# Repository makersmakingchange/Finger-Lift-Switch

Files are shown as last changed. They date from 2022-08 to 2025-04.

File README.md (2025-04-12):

# Finger Lift Switch 
The Finger Lift Switch is an assistive switch that is activated by lifting a resting finger upwards. The switch activation distance is approximately 5 mm and the required force is about 5 grams-force.

Connect the cable to an assistive device with a 3.5 mm input jack. The user's lifting fingertip should be placed under the finger lift pad, resting on a lower surface or splint.
When the user raises their lifting finger, the finger lift lever will rotate and activate the switch. The switch will de-activate when the user lowers their lifting finger back to the resting surface. 

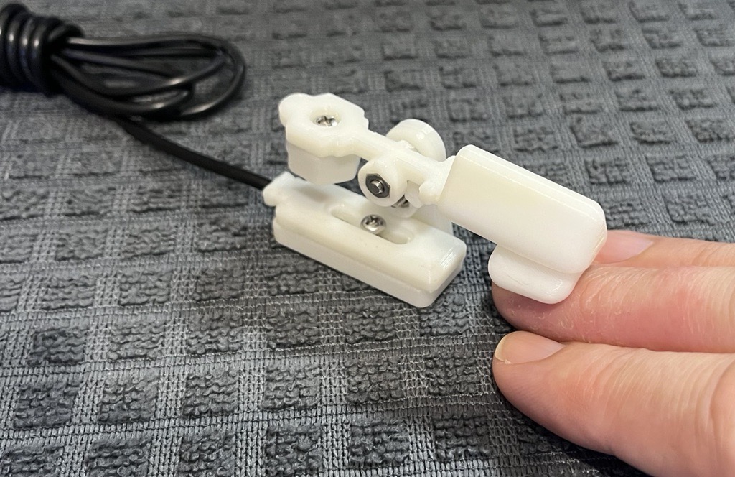
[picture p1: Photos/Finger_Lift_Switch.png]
Picture of Finger Lift Switch.


## More info at
- [Makers Making Change Project Page](https://makersmakingchange.com/project/finger-lift-switch/)

## How to Obtain a Finger Lift Switch
### 1. Do it Yourself (DIY) or Do it Together (DIT)

This is an open-source assistive technology, so anyone is free to build it. All of the files and instructions required to build the Finger Lift Switch are contained within this repository. Refer to the Maker Checklist below.

### 2. Request a build of this device

If you would like to obtain a Finger Lift Switch , you may submit a build request through the [MMC Library Page](https://makersmakingchange.com/project/finger-lift-switch/). The requestor is responsible for the cost of materials and any shipping.

### 3. How to build this device for someone else

If you have the skills and equipment to build this device, and would like to donate your time to create the switch for someone who needs it, visit the [MMC Maker Wanted](https://makersmakingchange.com/maker-wanted/) section.

## Getting Started

### 1. Read the Makers Checklist
Refer to the [Maker's Checklist](/Documentation/Finger_Lift_Switch_Maker_Checklist_v1.0.pdf) for an outline of the steps required to build the device.

### 2. Order the Off-The-Shelf Components

The [Bill of Materials](/Documentation/Finger_Lift_Switch_BOM_v1.0.xlsx) lists all of the parts and components required to build the device. The electronic and hardware component needs to be ordered online.

### 3. Print the 3D Printable components

All of the files and individual print files can be in the [/Build_Files/3D_Printing_Files](/Build_Files/3D_Printing/) folder.

### 4. Assemble the Finger Lift Switch

Reference the [Assembly Guide](/Documentation/Finger_Lift_Switch_Assembly_Guide_v1.0.pdf) for the tools and steps required to build each portion.

## Files
### Documentation
| Document             | Version | Link |
|----------------------|---------|------|
| Design Rationale     | 1.0     | [Finger_Lift_Switch_Design_Rationale](/Documentation/Finger_Lift_Switch_Design_Rationale_v1.0.pdf)     |
| Maker Checklist      | 1.0     | [Finger_Lift_Switch_Maker_Checklist](/Documentation/Finger_Lift_Switch_Maker_Checklist_v1.0.pdf)     |
| Bill of Materials    | 1.0     | [Finger_Lift_Switch_Bill_of_Materials](/Documentation/Finger_Lift_Switch_BOM_v1.0.xlsx)     |
| 3D Printing Guide    | 1.0     | [Finger_Lift_Switch_3D_Printing_Guide](/Documentation/Finger_Lift_Switch_3D_Printing_Guide_v1.0.pdf)     |
| Assembly Guide       | 1.0     | [Finger_Lift_Switch_Assembly_Guide](/Documentation/Finger_Lift_Switch_Assembly_Guide_v1.0.pdf)     |
| User Guide           | 1.0     | [Finger_Lift_Switch_User_Guide](/Documentation/Finger_Lift_Switch_User_Guide_v1.0.pdf)    |
| Changelog            | 1.0     | [Finger_Lift_Switch_Changelog](/Documentation/Finger_Lift_Switch_Changelog_v1.0.pdf)     |

### Design Files
[CAD Files](/Design_Files)

### Build Files
 - [3D Printing Files](/Build_Files/3D_Printing)

## Attribution
Designed by Makers Making Change (Derrick Andrews) in conjunction with Sunnyhill.

## License
Everything needed or used to design, make, test, or prepare the Low Profile Switch is licensed under the CERN 2.0 Permissive license <https://ohwr.org/project/cernohl/wikis/Documents/CERN-OHL-version-2> (CERN-OHL-P) . 

Accompanying material such as instruction manuals, videos, and other copyrightable works that are useful but not necessary to design, make, test, or prepare the Low Profile Switch are published under a Creative Commons Attribution-ShareAlike 4.0 license https://creativecommons.org/licenses/by-sa/4.0/ (CC BY-SA 4.0).

---
<!-- ABOUT MMC START -->
## About Makers Making Change
[Makers Making Change Logo](https://www.makersmakingchange.com/)

Makers Making Change is a program of [Neil Squire](https://www.neilsquire.ca/), a Canadian non-profit that uses technology, knowledge, and passion to empower people with disabilities.

Makers Making Change leverages the capacity of community based Makers, Disability Professionals and Volunteers to develop and deliver affordable Open Source Assistive Technologies.

 - Website: [www.MakersMakingChange.com](https://www.makersmakingchange.com/)
 - GitHub: [makersmakingchange](https://github.com/makersmakingchange)
 - Bluesky: [@makersmakingchange.bsky.social](https://bsky.app/profile/makersmakingchange.bsky.social)
 - Instagram: [@makersmakingchange](https://www.instagram.com/makersmakingchange)
 - Facebook: [makersmakechange](https://www.facebook.com/makersmakechange)
 - LinkedIn: [Neil Squire Society](https://www.linkedin.com/company/neil-squire-society/)
 - Thingiverse: [makersmakingchange](https://www.thingiverse.com/makersmakingchange/about)
 - Printables: [MakersMakingChange](https://www.printables.com/@MakersMakingChange)

### Contact Us
For technical questions, to get involved, or to share your experience we encourage you to [visit our website](https://www.makersmakingchange.com/) or [contact us](https://www.makersmakingchange.com/s/contact).
<!-- ABOUT MMC END -->

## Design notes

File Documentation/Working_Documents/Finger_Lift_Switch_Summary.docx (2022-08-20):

# Title

Finger Lift Switch

## Subtitle

<Short description>

## Device Specifications

Build Time:

< 1hr

1-4 hr

5-10hr

>10hr

Cost:

$0 - $10

$11 - $25

$26 - $50

$51 - $100

$101 - $250

$250+

Stage: Recently Added

Skills: 3D Printing, Soldering

Need: Mobility, Agility/Dexterity

Disability: Mobility / Physical

Difficulty: Intermediate

License: CC-BY-SA

Usages: Environmental Controls, Computer Access, Communication Aids (AAC), Recreation and Leisure

Type: Assistive Switches

Designer: Derrick Andrews

## Device Details

### Overview

The Finger Lift Switch is an assistive switch that is activated by lifting a resting finger upwards. The switch activation distance is approximately 5 mm and the required force is about 5 grams-force.

### Usage

Connect the cable to an assistive device with a 3.5 mm input jack. The user’s lifting fingertip should be placed under the finger lift pad, resting on a lower surface or splint.

When the user raises their lifting finger, the finger lift lever will rotate and activate the switch. The switch will de-activate when the user lowers their lifting finger back to the resting surface.

### Cost

The cost of components for a single switch is approximately $11 CAD. However, obtaining the minimum quantities for a single build will bring the materials costs to $66 CAD.

### Build Instructions

The Finger Lift Switch consists of 3D printed parts and electronic components. The Assembly Guide is available at the GitHub repository.

#### Skills Required

- 3D Printing
- Soldering
- Assembling screws

#### Time Required

3D Printing Time: 1hr 30m

Assembly Time: 30m

#### Tools

- Soldering Iron (fine tip)
- 60/40 rosin core electrical solder
- Medium size Phillips screwdriver (type #1)
- Side cutters
- Wire strippers
- Super glue (gel type is best)
- Hot melt glue gun (low temp type)
- Permanent felt marker (fine tip)
- Needle nose pliers
- Sturdy metal tweezers
- Multimeter (with continuity reading capability)

#### Components

- 1X Ball Bearing: Type MR85ZZ (8 mm OD 5 mm ID)
- 2X 5 mm x 1 mm Magnets (Neodymium)
- 1X Reed Switch (Glass) Contact Normally Open (N/O) Magnetic Induction Switch (2 mm × 14 mm)
- 2X M3 x 8 mm Stainless Steel screws (Base & Base Cap screws)
- 1X M3 x 10 mm Stainless Steel screw (Counterweight screw)
- 1X M3 x 12 mm Stainless Steel screw (Bearing Screw)
- 1X M3 x 16 mm Stainless Steel screw (Balance screw)
- 5X M3 Stainless Steel Nut
- 1X 1/4-20 (Imperial size) Nut
- 1X 5-foot mono audio cable with 3.5 mm male phono plug

#### 3D Printing

- 1X Finger Lift Lever (3D)
- 1X Balance Screw Holder (3D)
- 1X Counterweight Nut Holder (3D)
- 1X Bearing Base (3D)
- 1X Bearing Base Cap (3D)
- 1X Reed Switch Plate (3D)

### Design

This design was created using OpenSCAD.

### Attribution

Designed by Makers Making Change (Derrick Andrews) in conjunction with Sunnyhill.

© 2022 by Neil Squire. This work is licensed under the CC BY SA 4.0 License: http://creativecommons.org/licenses/by-sa/4.0 Files available at https://makersmakingchange.com/project/finger-lift-switch/ Page 1 of 2

V1.0 | JULY 2022 Finger Lift Switch Summary

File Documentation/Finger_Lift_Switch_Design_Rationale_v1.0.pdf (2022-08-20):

V1.0 | July 2022

## FINGER LIFT SWITCH

## DESIGN RATIONALE

© 2022 by <Neil Squire Society >. This work is licensed under the CC BY SA 4.0 License: http://creativecommons.org/licenses/by-sa/4.0
Files available at https://makersmakingchange.com/project/finger-lift-switch/ | Page 1 of 6

### Introduction

The Finger Lift Switch was born from the request of Occupational Therapists working at SunnyHill Children’s Hospital in Vancouver British Columbia. The OTs were seeking an assistive switch capable of being operated by a very young child, who was unable to press down on conventional push button assistive switches. It was noticed that the child was able to lift some finger, albeit, with minimal force.

The intended users of the MMC Finger Lift Switch are people who experienced difficulties pressing downwards on conventional switches, but are able to lift fingers, even with minimal limited force.

### Research

While there appear to be no commercial switches that function via finger lifting action directly, there are low force switches that can be operated by a finger with low force.

The “Wearable Finger Switch for Dexterity” sold by Rehab Mart. The Finger Switch by Enabling Devices. The Finger Switch was billed as “A wearable switch for persons with limited mobility. The slightest movement on the switch activates a device” The Finger Switch uses a small metal rod connected to a limit switch, with a 3.5 mm mono cable to trigger to any suitable device. The switch is constructed from a small 1 inch square by half inch injection molded case.

https://www.rehabmart.com/product/finger-switch-32073.html

The “Adaptive Finger Switch” by GlassOuse

https://glassouse.com/product-category/g-switch-series

The Lift Switch by Stan Cassidy Centre for Rehabilitation (SCCR)

http//www.stancassidy.ca

This is not an actual lift switch, but a switch output inverter, which makes the output state of the switch into its opposite. Note, that virtually all switch inverter circuits register as “on” when the user is not present, as their finger (or hand) is not resting on the switch to maintain the “off” state. This could be problematic in some situations.

## DESIGN RATIONALE

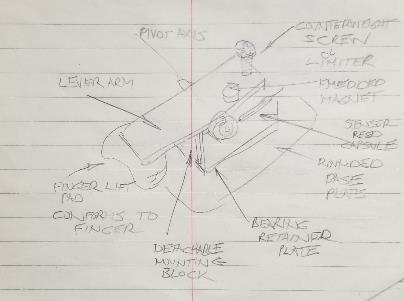
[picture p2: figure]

Files available at https://makersmakingchange.com/project/finger-lift-switch/ | Page 2 of 6

### Requirements

### Goals

G01 | An assistive switch that is activated by a finger lifting action.
G02 | To make the switch operate with minimal force, as in nearly unnoticeable to the user.
G03 | To make the switch operable in many different orientations i.e., minimally sensitive to gravity.

### Functional Requirements

F01 | The switch must activate when a finger lift is detected, but not when user’s hand is removed.
F02 | The switch must operate at angles from zero to at least 45 degrees from horizontal
F03 | The switch must be capable of activation with an operator force of less than 1 gram.

### Non-functional Requirement

NF0 1 | The switch should be narrow enough to allow at least 3 such switches to be operated by a user’s hand, though ideally, 5 (one for every finger).
NF0 2 | The switch must not require a battery.

### Constraints

C01 | The MMC Finger Lift Switch must be able to be constructed using basic ‘maker’ tools.
C02 | The MMC Finger Lift Switch should be able to be disinfected using detergent and alcohol.

### Ideation

Early sketch based on discussion of requirements, with staff from Sunny Hill Children’s Hospital.

## DESIGN RATIONALE

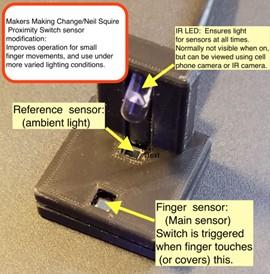
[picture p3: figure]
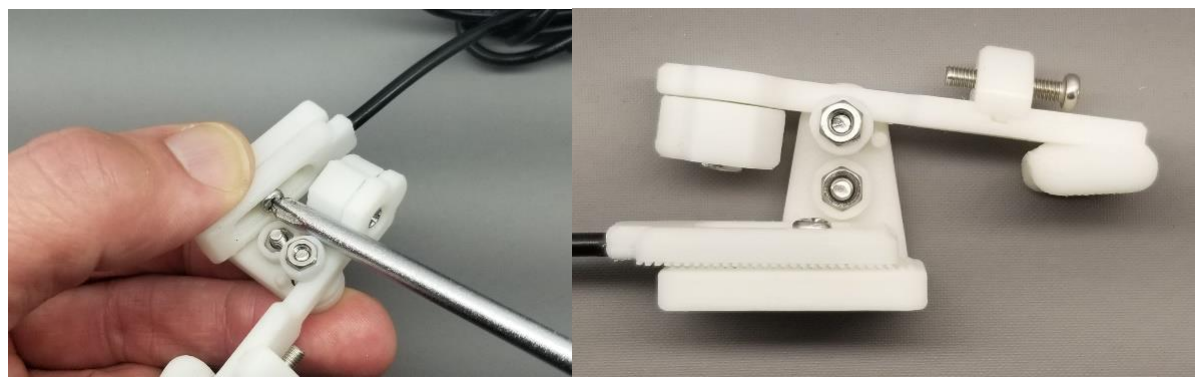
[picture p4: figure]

Files available at https://makersmakingchange.com/project/finger-lift-switch/ | Page 3 of 6

### Conceptual Design

### Concept 1

An initial electronic design of the Finger Lift Switch was created based on parameters given by the occupational therapist of the intended user. The original device was created using scraps of laser cut acrylic, nylon bushing, magnet, and a reed switch. The goal would be to create a final version using 3D printing methods.

### Concept 2

From a video of the user operating the initial optical design, it was determined the user had enough finger strength to operate a finger lever created based on a child’s ability to lift a finger 8 mm (as determined by occupational therapist of the intended user). The original reed switch version was created using scraps of laser cut acrylic, nylon bushing, and a reed switch. The goal would be to create a final version using 3D printing methods.

### Concept 3

## DESIGN RATIONALE

Files available at https://makersmakingchange.com/project/finger-lift-switch/ | Page 4 of 6

### Prototyping

The first iteration was built quickly, using scrap laser cut plastic parts. It was never intended for long term use, but rather, confirming the method of operation would work for the intended recipient. With feedback from Sunny Hill staff, it became clear the switch was easy to operate for the user, but it would benefit from a longer lever arm and proper bearing, instead of a bushing. It also became clear that making a 3D printable version would be worth the effort.

The second iteration was also the first of the 3D printed versions of the Finger Lift switch. It had a longer lever arm, with an integrated finger pad. It only needed a single magnet to trigger the reed switch, as it still relied on a counterweight to return the lever to the default position.

The use of a bushing worked well in the first implementation and was close to being chosen as the main method of rotation. However, when the design was upscaled the design had issues with the lever sliding out of position on the bushing, so the design was changed to incorporate a bearing instead.

The final major design change was the addition of the magnetic lever return. This came about because the occupational therapist requesting the switch, wanted to try mounting the switch on a hand splint at an angle. When they did so, the counterweight no longer exerted the same degree of force on the lever arm, and the lever arm would become sluggish or end up getting stuck in position. With realization that the switch would be more versatile if orientation wasn’t an issue, the decision was made to change to some form of spring return. Using a pair of repelling magnets seemed like a natural fit, as one magnet was already needed for activation of the reed switch, and the magnets usually came in packages of 10 or more. What’s more, the “spring” repulsion force could be arbitrary, by adjusting the gap between the magnets. To top it all off, using two magnets turned out to be rather serendipitous, as the fixed repulsion magnet primed the reed switch, improving its sensitivity, and making switch return less “sticky”.

## DESIGN RATIONALE

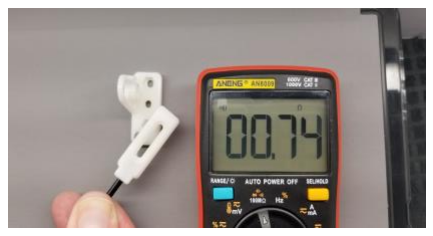
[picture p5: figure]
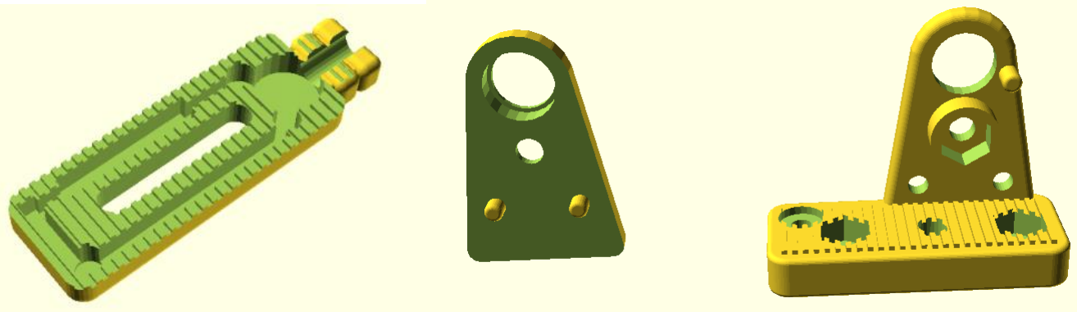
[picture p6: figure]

Files available at https://makersmakingchange.com/project/finger-lift-switch/ | Page 5 of 6

### Testing

### Detailed Design

During operation of the switch, it was noted that the lever arm finger pad sat lower than desired, making it awkward to initially place the user’s finger under the pad. A small post was added in the 3D CAD file to limit the lower end travel of the lever arm. With this change, there is always room under the finger pad to insert a finger prior to use.

### Design Review Improvements

Based on a group design review in July of 2022, several changes were made to the lift switch design. These changes were made for easier assembly, and less chance of breaking the delicate reed switch during construction. The changes made were:

- Widen base, reed switch plate, and solder area cups, to allow easier soldering of the reed switch.
- Remove requirement to bend reed switch wires (reed switch is very brittle glass), and instead, cut the reed switch wires using a jig to set the wire length.
- Trap the balance adjustment screw so it can’t fall out and become a choking hazard.

## DESIGN RATIONALE

Files available at https://makersmakingchange.com/project/finger-lift-switch/ | Page 6 of 6

### Further Opportunities for Improvement

- Change 3D design to minimize number of different screw sizes needed.
- Optimize 3D design and printer placement to produce cleaner holes and minimize the need to trim off excess material i.e., hexagonal holes and increased clearances.
- Placing a screw in the lever arm to allow finger pad resting position to be adjustable.
- Make a version of the switch that uses a readily available paperclip as a bushing, instead of a more difficult to source bearing.
- Allow calibration of the reed switch/magnet gap to be done using a screwdriver, instead of loosening a plate, and repositioning.

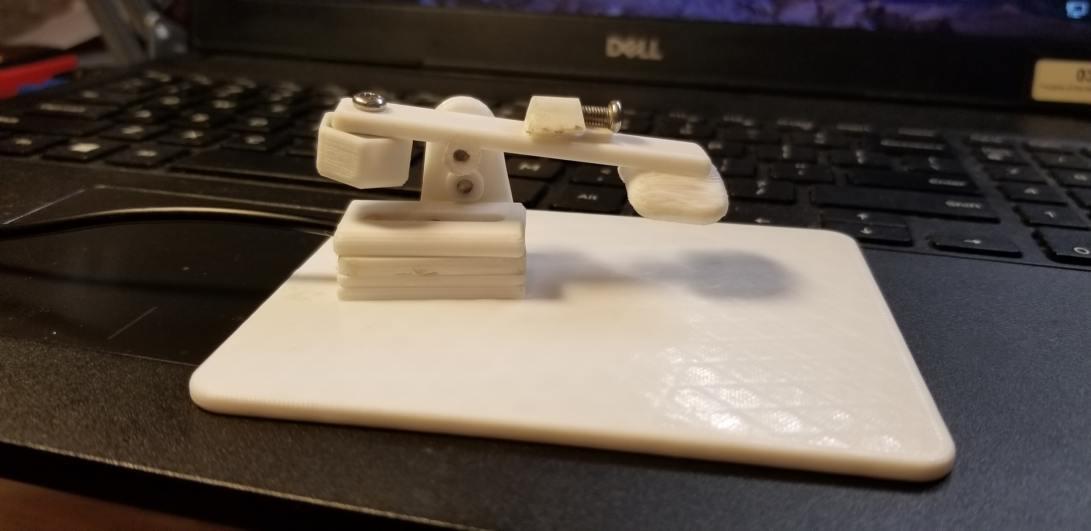
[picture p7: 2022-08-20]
Photos/Later_Finger_Lift_Switch_Prototype.jpg

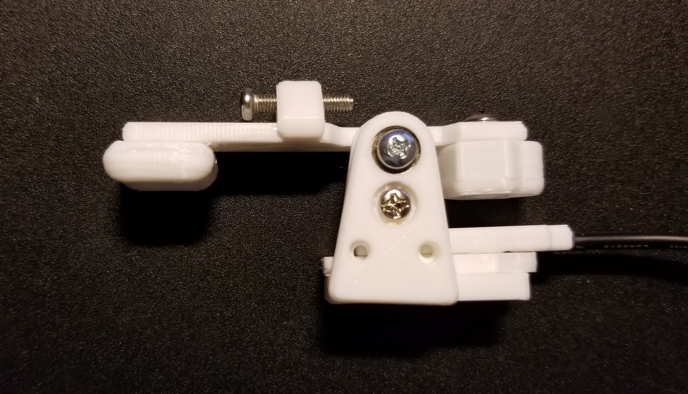
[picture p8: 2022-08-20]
Photos/Finger_Lift_Switch_side.jpg

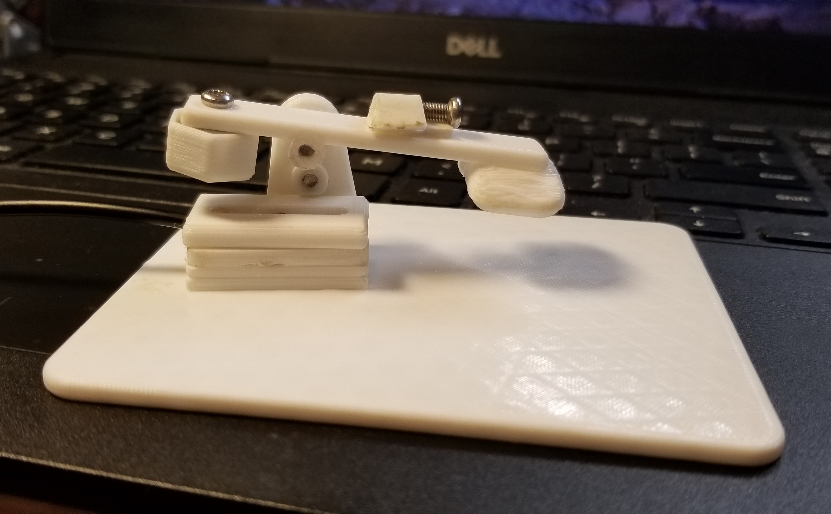
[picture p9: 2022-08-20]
Photos/Finger_Lift_Switch_later_prototype.jpg

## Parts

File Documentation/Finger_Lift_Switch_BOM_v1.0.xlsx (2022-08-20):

Finger Lift Switch for SunnyHill |  |  |  |  |  | $10.37 | $65.62
Part | Description | QTY | QTY/PKG | Min PKGs | Cost/PKG | Unit Cost | Total Cost | Source
Bearing, MR85-2RS, ID: 5 mm, OD: 8 mm, Thickness: 2.5 mm | Bearing | 1 | 10 | 1 | $14.14 | $1.41 | $14.14 | https://www.amazon.ca/MR85-2RS-Groove-Bearings-Double-Sealed/dp/B08JKG5D39
Reed Switch, 2 mm x 14 mm, Normally Open (N/O) | Reed Switch | 1 | 20 | 1 | $11.99 | $0.60 | $11.99 | https://www.amazon.ca/ARTGEAR-Contact-Normally-Magnetic-Induction/dp/B07V2YB2L3
M3 Screw & Nut Kit | M3 Screw & Nut Kit | 1 | 10 | 1 | $11.99 | $1.20 | $11.99 | https://www.amazon.ca/340pcs-Phillips-Stainless-Assortment-Thread/dp/B075RCVVYN?s=hi
Magnet, Neodymium, 5x1mm | Magnet | 2 | 200 | 1 | $13.99 | $0.14 | $13.99 | https://www.amazon.ca/Multi-Use-Refrigerators-Magnets-Whiteboard-Bulletin/dp/B07JDBLVBZ
Nut, 1/4 - 20 medium strength steel hex nut, zinc plated | Mounting Nut | 1 | 1 | 1 | $0.12 | $0.12 | $0.12 | https://www.homedepot.ca/product/paulin-1-4-20-inch-finished-hex-nut-zinc-plated-grade-5-unc-50pcs/1000123233
Cable, M/M, 3.5 mm mono, 10 ft | Mono cable | 1 | 2 | 1 | $12.99 | $6.50 | $12.99 | https://www.amazon.ca/TNP-3-5mm-Mono-Cable-10FT/dp/B01M3NBUD1
Filament, PLA, 1.7 mm, 3850 mm | filament @ $34.99/Kg Density 1.24g/cm3 No Markups | 1 | 1 | 1 | $0.40 | $0.40 | $0.40 | https://www.ic3dprinters.com/3d-printer-job-cost-calculator/#_calc-anchor

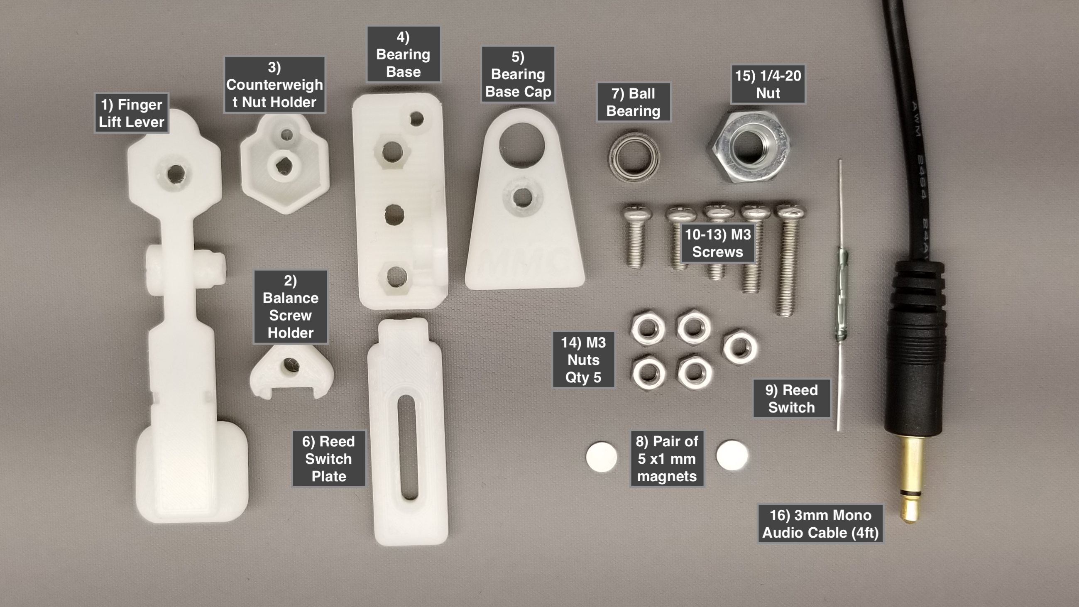
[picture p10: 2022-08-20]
Photos/1_All_Finger_Lift_Switch_parts.jpg

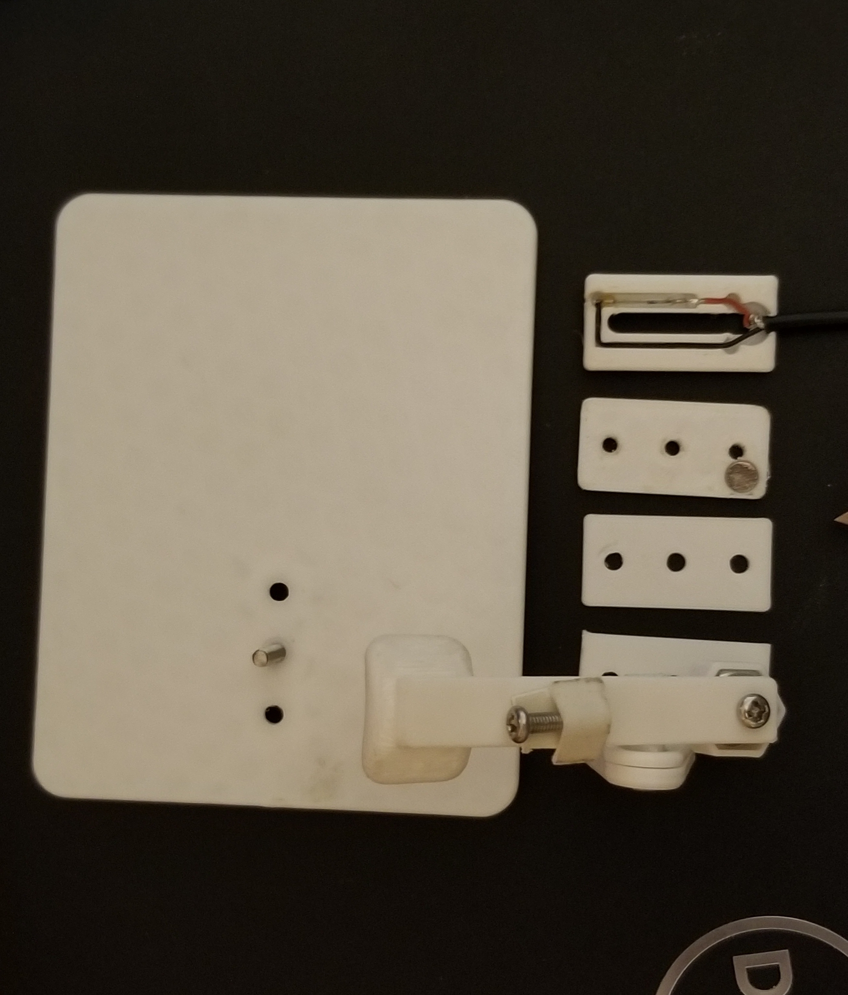
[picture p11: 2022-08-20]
Photos/Later_Finger_Lift_Switch_Parts_set.jpg

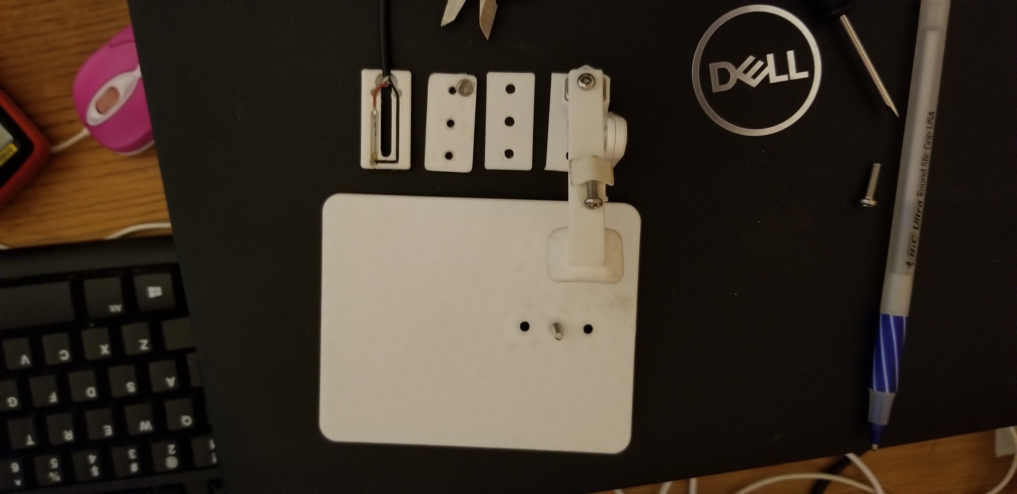
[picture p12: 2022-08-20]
Photos/Early_3D_Switch_Components.jpg

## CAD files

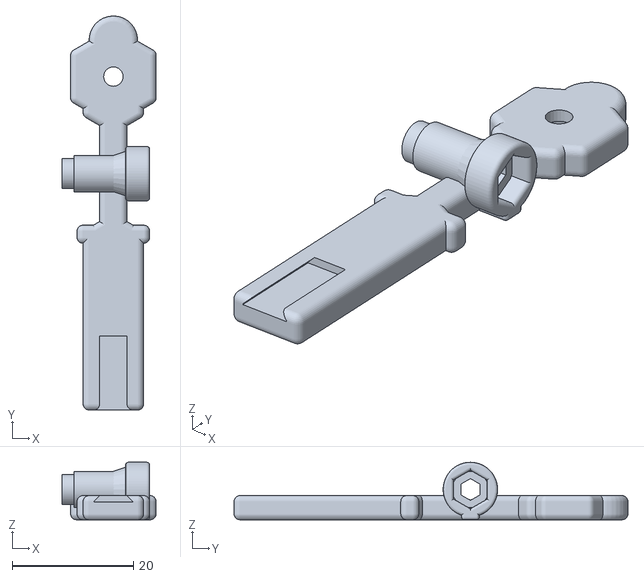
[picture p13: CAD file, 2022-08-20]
Build_Files/3D_Print_Files/FingerLiftArmFn.stl
15.6 x 65.0 x 9.49

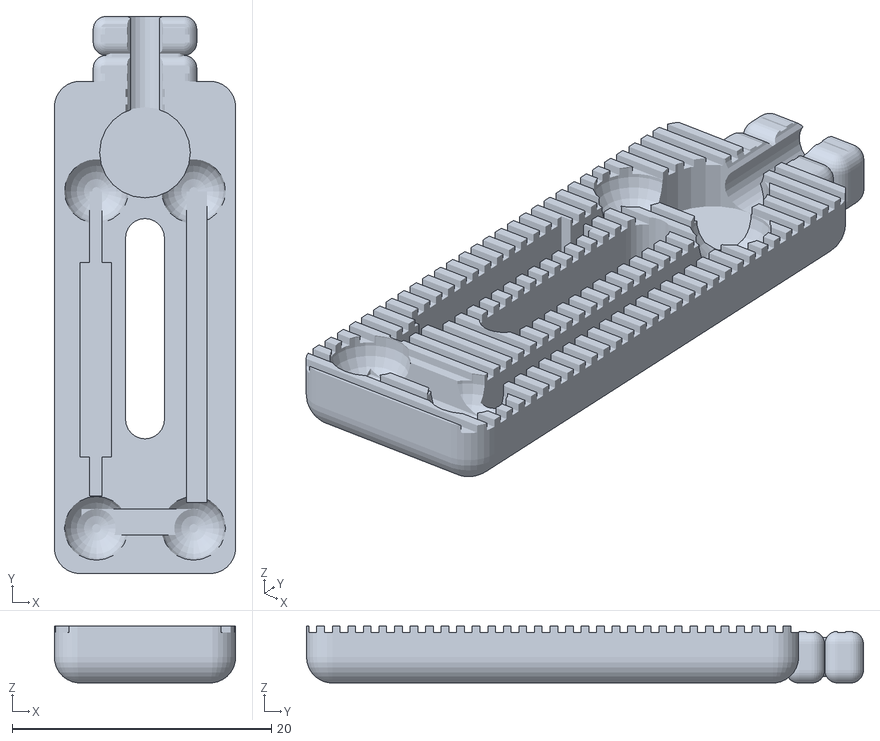
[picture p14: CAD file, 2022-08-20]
Build_Files/3D_Print_Files/ReedSwitchPlateWideFn.stl
14.0 x 43.0 x 4.39

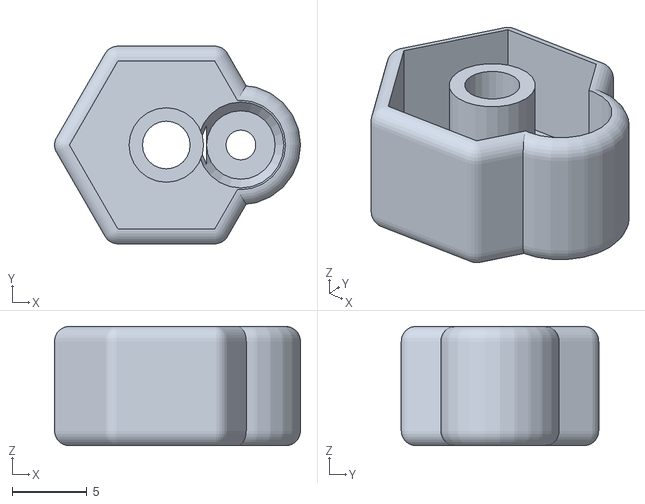
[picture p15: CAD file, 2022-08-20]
Build_Files/3D_Print_Files/CounterWeightHolderFn.stl
16.5 x 13.2 x 7.99

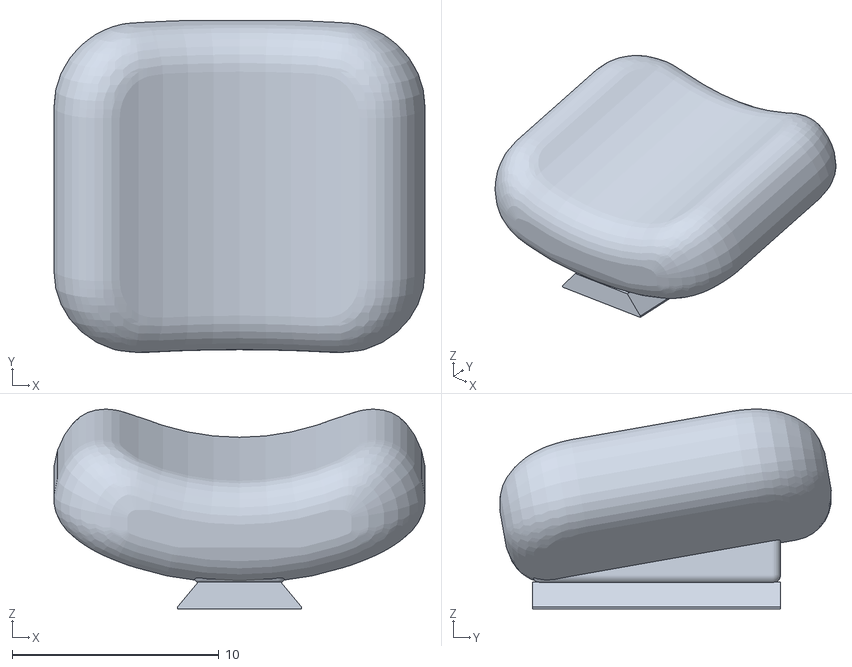
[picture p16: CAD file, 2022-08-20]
Build_Files/3D_Print_Files/FingerLiftPadFn.stl
17.9 x 16.0 x 9.67

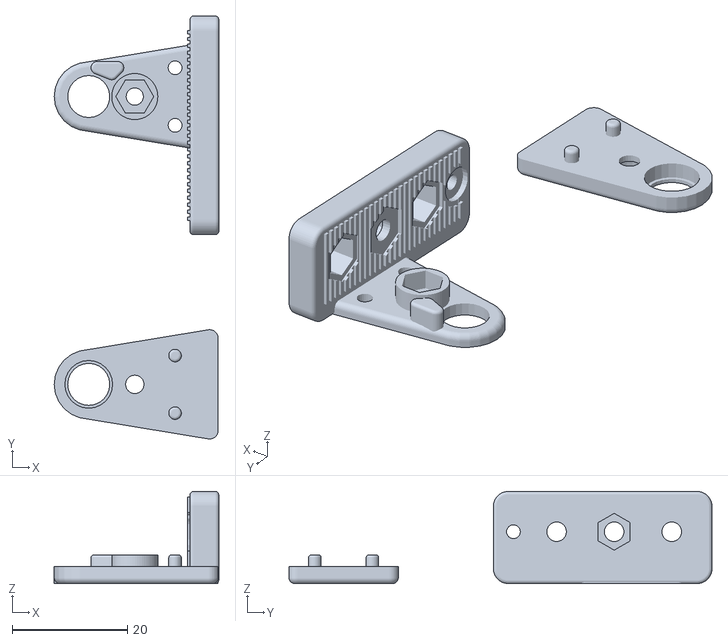
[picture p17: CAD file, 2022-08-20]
Build_Files/3D_Print_Files/FingerBearingBaseFn.stl
28.6 x 73.5 x 16.0

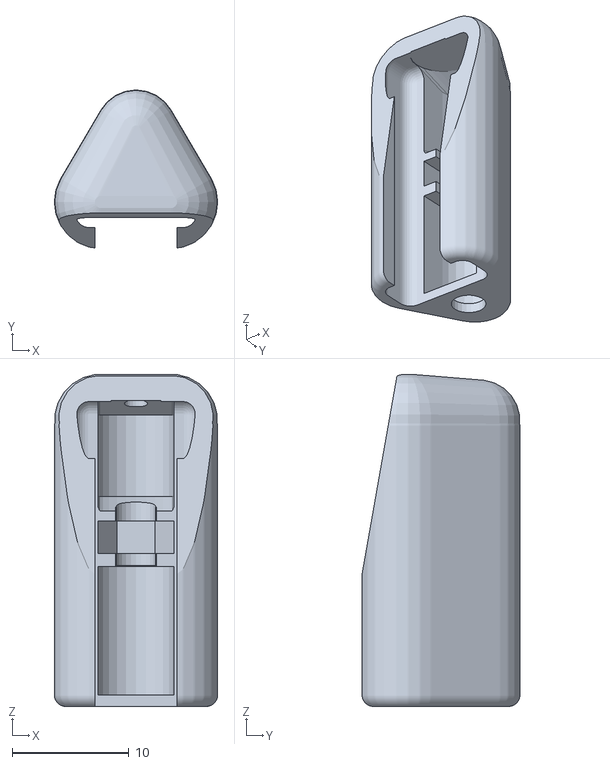
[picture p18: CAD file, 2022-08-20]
Build_Files/3D_Print_Files/BalanceScrewHolderFn.stl
14.0 x 13.5 x 28.5

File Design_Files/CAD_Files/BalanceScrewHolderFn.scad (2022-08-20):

$fn=60;	
holderHeight = 23;

hullDiam=5; //Hull radius diam
balScrewDiam = 3+.4; //Hole for M3 screw + fudge factor
balScrewHeadfDiam = 5.6; //Hole for M3 screw + fudge factor
minkRad = 1;
difference(){

union(){
//FRONT END (hulled)
translate ([0,0,5/2+10])hull() { //nice rounded front end
translate([0,-3.5+5.6,0])sphere(d=hullDiam+2, center = true,$fn=24);//
translate([-3,-4,0])sphere(d=hullDiam+3, center = true,$fn=24);//
translate([3,-4,0])sphere(d=hullDiam+3, center = true,$fn=24);//
}//hull

translate ([0,0,-2])minkowski(){	//TRIANGULAR TUBE
translate ([0,0,5/2])hull() { //rounded bearing mount
translate([0,-3.5+5.6,0])cylinder(d=hullDiam,h=holderHeight, center = true,$fn=24);//
translate([-3,-4,0])cylinder(d=hullDiam+1,h=holderHeight, center = true,$fn=24);//
translate([3,-4,0])cylinder(d=hullDiam+1,h=holderHeight, center = true,$fn=24);//
	
//CircleItems(3,5,30+180)cylinder(d=3,h=5, center = true,$fn=24);//
 
}//hull
sphere(minkRad);


}//minkowski
}//union
//Removals:

//translate([0,-3.5,5.2/2])cube([10.2,3,10], center = true);//original lever cutout
translate([0,-8,5.2/2])cube([7,5,holderHeight+10], center = true);//bottom end cutout for nut access

translate([0,-4,-1])rotate([90,0,0])cutOutSlug();//chop out balance beam area
translate([0,-4.5+5.6,5.2/2])cylinder(d=balScrewDiam,h=10, center = true,$fn=24);//m3 screw holder
translate([0,-4.5+5.6,5.2/2+8.5])cylinder(d=balScrewHDiam,h=9, center = true,$fn=24);//m3 screw Head top
translate([0,-4.5+5.6,5.2/2-8.5+1])cylinder(d=balScrewHeadfDiam,h=10, center = true,$fn=24);//m3 screw Head bottom

translate([0,-4.5+5.6,-12])cylinder(d=balScrewDiam,h=10, center = true,$fn=24);//Screwdriver head access 

translate([0,-4.5+5.6,2.5])rotate([0,0,0])hull(){
cylinder(d=6.5,h=2.8, center = true,$fn=6);//nut cutout
translate([0,-4,0])cylinder(d=6.5,h=2.8, center = true,$fn=6);//nut cutout shifted to make insertion channel
}//hull


//create front screw shaft access 
translate([0,-4.5+5.6,9.5])rotate([0,0,0])hull(){
cylinder(d=6.5,h=7, center = true,$fn=24);//nut cutout
translate([0,-4,0])cylinder(d=6.5,h=9.5, center = true,$fn=24);//nut cutout shifted to make insertion channel
}//hull

//create rear screw head access
translate([0,-4.5+5.6,-5.5])rotate([0,0,0])hull(){
cylinder(d=6.5,h=11, center = true,$fn=24);//nut cutout
translate([0,-4,0])cylinder(d=6.5,h=11, center = true,$fn=24);//nut cutout shifted to make insertion channel
}//hull

translate([0,-4,5.2/2+3])cube([3.5,10,holderHeight-10], center = true);//bottom end cutout for view
translate([0,-7.5,10.5])rotate([-10,0,0])cube([14,3,25], center = true);//angled chop off, to make room for finger lift pad

}//diff
//test area


//
//test nut dummy
//translate([0,-4.5+5.6,2.5])rotate([0,0,0])cylinder(d=6.5,h=2.8, center = true,$fn=6);//nut cutout
//*********** MODULES *****************************

module cutOutSlug(){

difference(){
minkowski(){
translate([0,0,0])roundedCube (8,holderHeight+5,2,0);
 sphere(r=1.2,center=true,$fn=30);//added .2 to loosen grip
}// Mink
//"hard" removals (no rounding) 

//translate([-4.5,0,-1])cube([2,2,3], center = true);
//translate([4.5,0,-1])cube([2,2,3], center = true);
}// diff
}//module


module CircleItems(n,r,myRot)
{
segment=360 / n;
for (i=[1:n])
{
rotate([0, 0, segment*i+myRot])
translate ([r,0,0])
children();
}//for
}//module


module roundedCube (myBoxWidth,myBoxDepth,myBoxHeight,minkRadius)
//** maintains proper 'cube' dimensions due to compensation for object expansion 
//** that normally occurs while using Minkowski operations in OpenSCAD)
{

translate([0,0,0])minkowski(){
cube([myBoxWidth-minkRadius*2,myBoxDepth-minkRadius*2,myBoxHeight-minkRadius*2], center = true);
sphere(r=minkRadius,center=true,$fn=30);
}  //end mink

}//end module roundBottomCube
	
	

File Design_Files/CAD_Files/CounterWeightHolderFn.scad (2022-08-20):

//Software : Counter Weight Holder (component: CounterWeightHolder)
//Developed by : MakersMakingChange  A Neil Squire Society Program
// Code Type: Written in OpenSCAD, a code based, open source 3D CAD modeling environment.
//Original Author: Derrick Andrews
//VERSION: 2.2-beta (July 2022) 
//Copyright Neil Squire Society 2022. 
//LICENSE: This work is licensed under the CC BY SA 4.0 License: http://creativecommons.org/licenses/by-sa/4.0 .

difference(){
	minkowski(){	
	    union(){
		translate([0,0,8/2]) cylinder(d=13,h=6, center = true,$fn=6);//counterweight nut cutout
	    translate([5,0,8/2])cylinder(d=6,h=6, center = true,$fn=24);//magnet cutout
			}//union
		sphere(r=1,center=true,$fn=30);
}  //end mink	n
   //removals
	translate([5,0,8/2+2])cylinder(d=6,h=8, center = true,$fn=24);//**magnet drop in chute
translate([0,0,8/2+2]) cylinder(d=13,h=8, center = true,$fn=6);//counterweight nut cutout

translate([5,0,1.2/2+1])cylinder(d1=4.6,d2=6,h=1.2, center = true,$fn=24);//magnet cutout
 translate([5,0,0])cylinder(d=2,h=10, center = true,$fn=24);//magnet release
cylinder(d=3.2,h=5, center = true,$fn=24);//M3 screw hole
cylinder(d=3.2,h=8, center = true,$fn=24);//M3 screw hole
translate([0,0,-.5])rotate([0,0,30])cylinder(d=6.2,h=2.1, center = false,$fn=6);//M3 nut capture  hole
}
 translate([0,0,5])difference(){

 cylinder(d=5,h=6, center = true,$fn=24);//M3 screw hole
  cylinder(d=3.2,h=6, center = true,$fn=24);//M3 screw hole
	}

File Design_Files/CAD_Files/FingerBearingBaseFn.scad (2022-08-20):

baseBlockHeight =5;
nutPocketHeight =2.4+.6+1;// M3 nut height in mm with .6 extra clearance
nutHexDiam =6 +.4 ; 
//translate([10,73,9])rotate([0,270,180])import("/Users/derrickandrews/My Drive/NSS Office/MMC Finger Lift Review Improvements /ReedSwitchPlateWideProto.stl");


translate([0,0,0])makeBearingCoverPlate();//accepts bearing 
translate([0,50,2])rotate([180,0,0]) makeBearingStand(); //Cover Plate goes on this portion of base
//translate([0,50,2])rotate([180,0,0]) makeBearingBaseOld(); //The main base block original narrow version
translate([7.5,47,9])rotate([180,270,180]) makeBearingBaseNew(); //The main base block wider version
//makeBearingBaseNew(); //The main base block wider version (base default centered here)


module makeBearingBaseNew()
{
difference(){	
union(){

minkowski(){
translate([-1,-2,3.8/2+.5])rotate([0,0,0]) sideRoundedCube(16-1.2,38-1.2,3.8,2);//even better with rounding
sphere(r=.6, center = true,$fn=30);
}  //end mink
translate([0,-2,4.8+.2])ArrayCentItemsVar(1,28,1,1.2)cube([12,.6,.6], center = true);
}//union

//Removals
ArrayCentItemsVar(1,3,0,10)cylinder(d=3.4,h=20, center = true,$fn=24);//Create line of 3 screw holes in base
translate([0,0,3/2-.2])cylinder(d=6.4,h=nutPocketHeight-.5, center = true,$fn=6);//Create center lower nut catch
translate([0,0,(baseBlockHeight+.5)-nutPocketHeight/2+.01])ArrayCentItemsVar(1,2,0,20)cylinder(d=6.4,h=nutPocketHeight, center = true,$fn=6);////Create upper (outer) nut catches

translate([0,0,baseBlockHeight+.2])ArrayCentItemsVar(1,3,0,10)cylinder(d=6.4+2,h=1, center = true,$fn=6);//Remove grip from around screw holes
translate([0,-17.5,5])cylinder(d=5.4,h=2, center = true,$fn=24);//Bore magnet recess
translate([0,-17.5,6])cylinder(d=7,h=2.2, center = true,$fn=24);//Bore magnet recess
translate([0,-17.5,6])cylinder(d=2.4,h=20, center = true,$fn=24);//Create magnet release hole in base
}//diff	
//test cube([14,36,14], center = true);
}



module makeBearingBaseOld()
{
difference(){	
union(){
//translate([6.6,5,-13/2])cube([2,30,17], center = true);	//original Base portion (printed vertically)
//translate([6.6-1.5,5+1,-13/2+1])cube([2+3,30+2,15], center = true);	//new fatter Base portion (printed vertically)
minkowski(){
translate([6.6-1.5,5+1,-13/2+1.5])rotate([90,0,90]) sideRoundedCube(34-1.2,14-1.2,5-1.2,2);//even better with rounding
sphere(r=.6,center=true,$fn=30);
}  //end mink
translate([2.4,6,-5.5])ArrayCentItemsVar(1,26,1,1.2)cube([.6,.6,10], center = true);
}

translate([0,-5-1,-6])rotate([0,90,0])cylinder(d=3.4,h=20, center = true,$fn=24);//Create front hole in base
translate([3.5,-5-1,-6])rotate([0,90,0])cylinder(d=6.4,h=4, center = true,$fn=6);//Bore front screw head countersink in base

translate([0,5-1,-6])rotate([0,90,0])cylinder(d=3.4,h=20, center = true,$fn=24);//Create center hole in base
translate([6.7,5-1,-6])rotate([0,90,0])cylinder(d=6.4,h=5, center = true,$fn=6);//Create center lower nut catch

translate([0,15-1,-6])rotate([0,90,0])cylinder(d=3.4,h=20, center = true,$fn=24);//Create rear hole in base
translate([3.5,15-1,-6])rotate([0,90,0])cylinder(d=6.4,h=4, center = true,$fn=6);//Bore rear screw head countersink in base
	
translate([0,15+4,-6+4])rotate([0,90,0])cylinder(d=2.4,h=20, center = true,$fn=24);//Create magnet release hole in base
//translate([0,15+4,-6+4])rotate([0,90,0])cylinder(d=2.4,h=20, center = true,$fn=24);//Create pseudo magnet 	
translate([2.5,15+4,-6+4])rotate([0,90,0])cylinder(d=5.4,h=2.2, center = true,$fn=24);//Bore magnet recess	

}	

}


module makeBearingCoverPlate()
{

difference(){
minkowski(){	
hull() { //rounded bearing mount
    translate([-15,0,4/2])cylinder(d=10,h=2, center = true,$fn=24);//
    translate([6,8,4/2])cylinder(d=1,h=2, center = true,$fn=24);//Create center side hole
	translate([6,-8,4/2])cylinder(d=1,h=2, center = true,$fn=24);//Create center side hole
}//hull
sphere(r=1,center=true,$fn=30);
}  //end mink
//removals
translate([0,0,3/2+3]) cube([50,30,3], center = true);
translate([-15,0,4/2])cylinder(d=7.3,h=4, center = true,$fn=24);//Create bearing catch hole
translate([-15,0,4/2+.6])cylinder(d=8.3,h=4, center = true,$fn=24);//Create bearing hole	

translate([-7,0,4/2]) cylinder(d=3.2,h=4, center = true,$fn=24);//Create plate cinch hole
translate([-7,0,2/2]) cylinder(d=6.6,h=2, center = true,$fn=24);//Create plate cinch head countersink
 //emboss text
 union(){
  translate([5.5,7.5,0.5])rotate([0,180,90]) linear_extrude(height = 5) {
       text(text = "MMC",font = "Liberation Sans:style=Bold Italic",size = 4.5);
     }//text 
}//union

}//difference


//translate([0,-5,3/2])cylinder(d=2,h=3, center = true,$fn=24);//test post
minkowski(){
translate([0,5,5/2])cylinder(d=1.2,h=4, center = true,$fn=24);//Create center side aligner pin
sphere(r=.5,center=true,$fn=30);
}  //end mink
minkowski(){
translate([0,-5,5/2])cylinder(d=1.2,h=4, center = true,$fn=24);//Create center side aligner pin
sphere(r=.5,center=true,$fn=30);
}  //end mink



}//end module make bearing plate


module makeBearingStand()
{


difference(){
minkowski(){	
hull() { //rounded bearing mount
    translate([-15,0,4/2])cylinder(d=10,h=2, center = true,$fn=24);//
    translate([6,8,4/2])cylinder(d=1,h=2, center = true,$fn=24);//Create center side hole
	translate([6,-8,4/2])cylinder(d=1,h=2, center = true,$fn=24);//Create center side hole
}//hull
sphere(r=1,center=true,$fn=30);
}  //end mink
//removals
translate([0,0,3/2+3]) cube([50,30,3], center = true);
translate([-15,0,4/2])cylinder(d=7.3,h=4, center = true,$fn=24);//Create bearing back catch bore
//translate([-15,0,4/2+.6])cylinder(d=8.3,h=4, center = true,$fn=24);//Create bearing holder bore if needed	
translate([0,5,3/2])cylinder(d=2.4,h=5, center = true,$fn=24);//Create center side hole
translate([0,-5,3/2])cylinder(d=2.4,h=5, center = true,$fn=24);//Create center side hole
translate([-7,0,4/2]) cylinder(d=3,h=4, center = true,$fn=24);//Create plate cinch hole
translate([-7,0,3/2+2]) cube([35,25,3], center = true);//remove unwanted bottom
}//difference
//translate([0,-5,3/2])cylinder(d=2,h=3, center = true,$fn=24);//test post

minkowski(){
difference(){
translate([-7,0,-1]) cylinder(d=7.75,h=4, center = true,$fn=60);//Create screw thread extension
translate([-7,0,0]) cylinder(d=6.4+1.2,h=10, center = true,$fn=6);//Create nut catch below bearing
}//diff
sphere(r=.5,center=true,$fn=30);
}  //end mink

//translate([-14,-5,-1]) cylinder(d=2,h=3, center = true,$fn=24);/Create lever drop limiter post 

minkowski(){
hull(){
translate([-14.5,-4.8,-2])cylinder(d=.8,h=6, center = true,$fn=24);////Create lever drop limiter post: top (rounded)
translate([-11,-4,-2])cylinder(d=.8,h=6, center = true,$fn=24);////Create lever drop limiter post: inside middle(rounded)
translate([-10,-5.6,-2])cylinder(d=.8,h=6, center = true,$fn=24);////Create lever drop limiter post: bottom (rounded)
}

sphere(r=.75,center=true,$fn=30);
}  //end mink

}//end module makeBearingStand()



module basicBox (myBoxWidth,myBoxDepth,myBoxHeight,myWallWidth)
{
difference(){	
cube([myBoxWidth,myBoxDepth,myBoxHeight], center = true); // Build box body
translate([0,0,myWallWidth+.01])cube([myBoxWidth-myWallWidth*2,myBoxDepth-myWallWidth*2,myBoxHeight-myWallWidth*2], center = true); // Mill out box cavity
}//end diff
}//end module basic box
	

module roundedBox (myBoxWidth,myBoxDepth,myBoxHeight,myWallWidth,minkRadius)
//creates hollow rounded bottom box IMPORTANT*** requires module roundBottomCube 
{
difference(){	
roundBottomCube (myBoxWidth,myBoxDepth,myBoxHeight,minkRadius); // Build box body
translate([0,0,myWallWidth+.01])roundBottomCube (myBoxWidth-myWallWidth*2,myBoxDepth-myWallWidth*2,myBoxHeight-myWallWidth*2,minkRadius); //Mill out box cavity
}//end diff
//translate([20,0,myWallWidth+.01])roundBottomCube (myBoxWidth-myWallWidth*2,myBoxDepth-myWallWidth*2,myBoxHeight-myWallWidth*2,minkRadius); // Mill out box cavity
//translate([20,0,myWallWidth+.01])roundBottomCube (myBoxWidth,myBoxDepth,myBoxHeight,minkRadius); // Build box body
}//end module rounded box

//roundBottomCube (myBoxWidth,myBoxDepth,myBoxHeight,minkRadius);


module roundBottomCube (myBoxWidth,myBoxDepth,myBoxHeight,minkRadius)
//** Same as regular cube, but with rounded sides and bottom
//** maintains proper 'cube' dimensions due to compensation for object expansion 
//** that normally occurs while using Minkowski operations in OpenSCAD)
{
union()
{
difference()
{
translate([0,0,minkRadius/2])minkowski(){
cube([myBoxWidth-minkRadius*2,myBoxDepth-minkRadius*2,myBoxHeight-minkRadius], center = true);//Main plate   original cube([90,testSize8,8.5]
sphere(r=minkRadius,center=true,$fn=30);
}  //end mink
translate([0,0,myBoxHeight/2+minkRadius/2]) cube([myBoxWidth,myBoxDepth,minkRadius], center = true);
}

}//end union
}//end module roundBottomCube

//test
//translate ([15,0,0])cube([35,35,35],center=true);
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

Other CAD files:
Design_Files/CAD_Files/FingerLiftArmFn.scad
Design_Files/CAD_Files/FingerLiftPadFn.scad
Design_Files/CAD_Files/ReedSwitchPlateWideFn.scad

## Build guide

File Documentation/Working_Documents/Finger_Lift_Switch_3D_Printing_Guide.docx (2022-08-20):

# 3D Printing Summary

Metrics
Total Print Time (min) | 1:23
Total Number of Components | 6
Typical Total Mass (g) | 7
Typical Number of Print Setups | 1

# 3D Printing Settings

Print File Name | Qty | Total Print Time (hr:min) | Mass (g) | Infill (%) | Support(Y/N) | Layer Height/ Nozzle Diameter(mm) | Notes (orientation, special settings, etc.)
Finger Lift Lever | 1 | 0:19 | 2 | 15 | N | 0.2/0.4 | - Print in orientation given in STL
Balance Screw Holder | 1 | 0:07 | 1 | 15 | N | 0.2/0.4 | - Print in orientation given in STL
Counterweight nut holder | 1 | 0:11 | 1 | 15 | N | 0.2/0.4 | - Print in orientation given in STL
Bearing Base & Bearing Base Cap | 1 | 0:29 | 2 | 15 | N | 0.2/0.4 | - Print in orientation given in STL
Reed Switch Plate | 1 | 0:10 | 1 | 15 | N | 0.2/0.4 | - Print in orientation given in STL

# Customization Options

Specific colours are not a requirement for this device, so device (or components) may be printed in whichever colours the user desires.

# Post-Processing

Remove any stranding or excess material in holes with a hobby knife. Any parts of the Finger Lift Pad that feel rough or scratchy should be lightly sanded with fine sandpaper until smooth to touch.

# Examples of Quality Prints

Finger Lift Lever

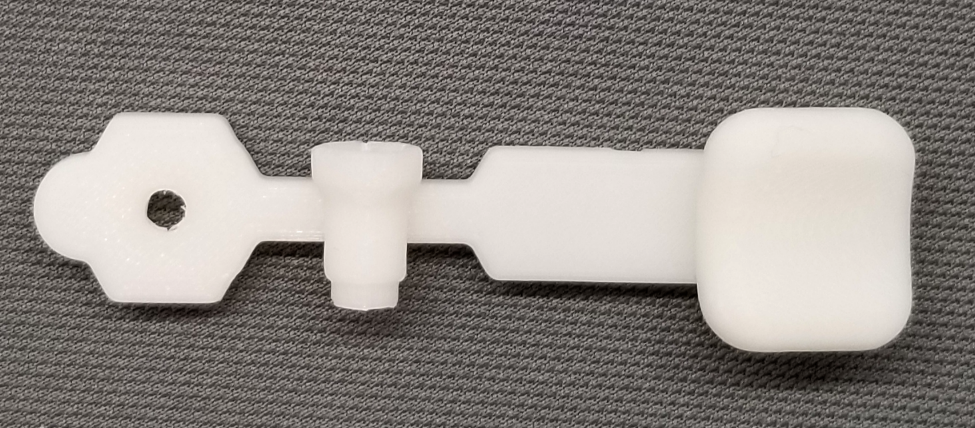
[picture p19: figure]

Bearing Base

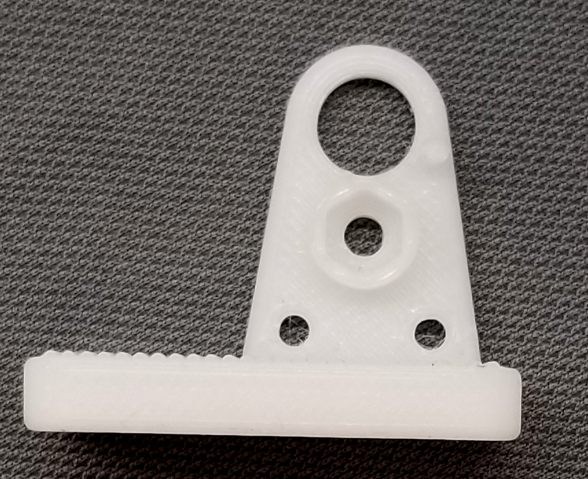
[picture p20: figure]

Reed Switch Plate

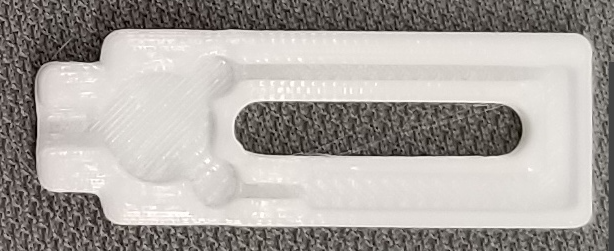
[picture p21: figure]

Bearing Base Cap

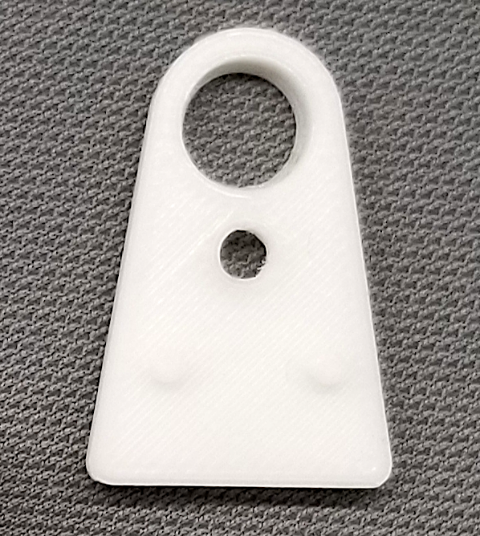
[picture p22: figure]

Balance Screw Holder

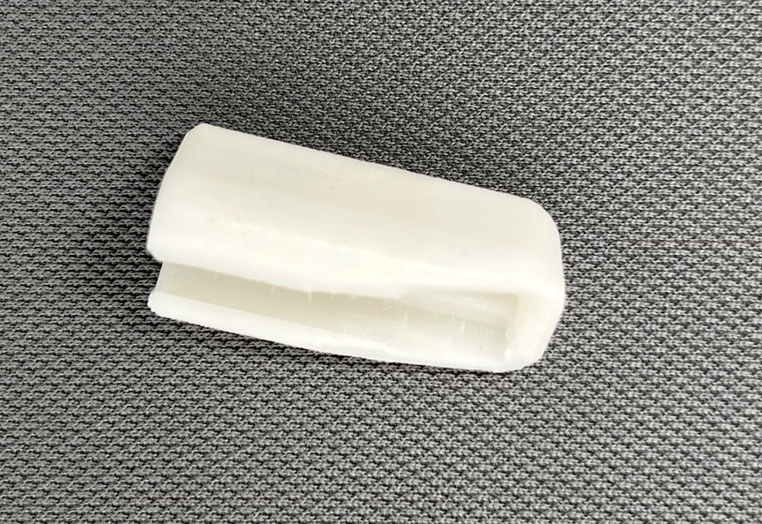
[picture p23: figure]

Counterweight nut holder

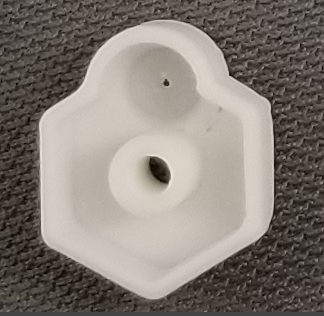
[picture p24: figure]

© 2022 by Neil Squire This work is licensed under the CC BY SA 4.0 License: http://creativecommons.org/licenses/by-sa/4.0 Files available at https://makersmakingchange.com/project/finger-lift-switch/ Page 1 of 2

V1.0 | July 2022 Finger Lift Switch 3D Printing Guide

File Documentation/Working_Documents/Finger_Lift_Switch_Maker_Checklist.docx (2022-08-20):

## Maker To Do

☐ Order Hardware Components

☐ Ask User about color preferences

☐ Print 3D Printed Components

- 1 x Finger Lift Lever
- 1 x Finger Lift PAD
- 1 x Balance screw holder
- Counterweight nut holder
- Bearing Base & Bearing Base Cap
- Reed Switch Plate

☐ Assemble Switch

☐ Test Switch

☐ Clean and package Switch

☐ Print out Finger Lift Switch: Quick Guide

# Items for the User

☐ Tested, cleaned, and packaged Finger Lift Switch

☐ Finger Lift Switch: Quick Guide

© 2022 by Neil Squire. “Finger Lift Switch Maker Checklist” is licensed under the CC BY SA 4.0 License: http://creativecommons.org/licenses/by-sa/4.0 PAGE PAGE \* MERGEFORMAT 1 OF NUMPAGES \* Arabic \* MERGEFORMAT 3 Design files available at https://www.makersmakingchange.com/project/finger-lift-s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

V1.0 | July 2022 Finger Lift Switch MAKER CHECKLIST

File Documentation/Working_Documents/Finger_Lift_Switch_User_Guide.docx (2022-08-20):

## Introduction

The Finger Lift Switch is an accessible switch with a single button finger lever. The switch is activated by placing a finger under the finger pad and lifting the finger until activation occurs. This device is suitable for anyone and can be connected to any device with a 3.5 mm interface.

## Features

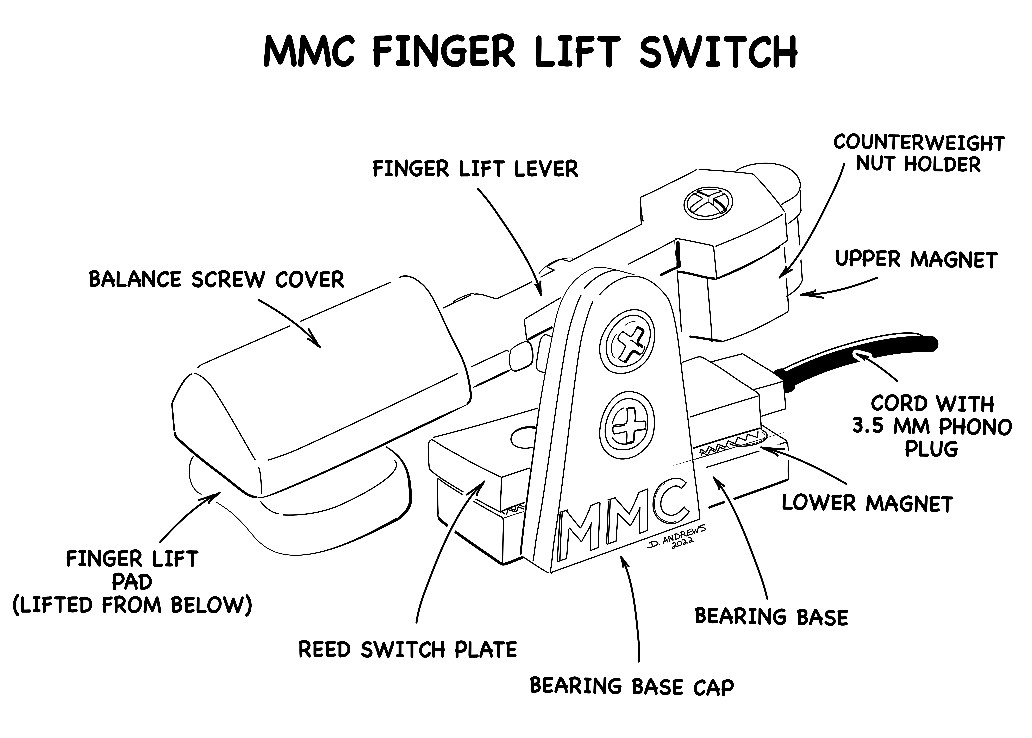
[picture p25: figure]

## Usage

Connect the cable to the assistive device. The user’s lifting fingertip should be placed under the finger lift pad, resting on a lower surface or splint. The switch is activated by the user raising their lifting finger and pressing against the finger lift pad from below. The switch will de-activate when the user lowers their lifting finger back to the resting surface. The switch activation distance will be approximately 5 mm.

Action | Action Time (seconds) | Function
Lifting Finger Pad using finger | < 1 | “On” Defined by interfaced device

## Compatibility

The Finger Lift Switch is compatible with any device that accepts a 3.5 mm mono plug. Note that this switch is intend for low current applications, such as computer or toy (digital) type inputs. Switching currents higher than 50 mA may cause the reed switch to become “sticky” (sluggish) or “stuck” (on all the time).

## Specifications

Activation Force | 0.05 ± 0.02 N 5 ± 2 grams-force
Activation Distance | ~5 mm
Dimensions (Length x Width x Height) | 85 x 20 x 35 mm
Weight | ~ 50 grams
Switch Capacity | 50 mA working at 24 VDC or VAC 1A max surge

## Cleaning

- Remove the lever arm, by unscrewing the bearing pivot screw. Note the position of the balance screw and remove it, placing it aside.
- Remove the counterweight screw and clean the counterweight separately. Counterweight should be wiped on the outside only. Never wet the internal nut, or it may rust.
- The plastic lever arm can be soaked in any water/detergent-based cleaning solution. Wipe dry.
- Wipe outside bearing base with a paper towel moistened in a mild water/detergent solution, or Lysol disinfecting wipe. Leave to dry completely to ensure that the internal reed switch element will not corrode.

© 2022 by Neil Squire. This work is licensed under the CC BY SA 4.0 License: http://creativecommons.org/licenses/by-sa/4.0 Files available at https://makersmakingchange.com/project/finger-lift-switch/ Page 2 of 3

V1.0 | July 2022 Finger Lift Switch user Quick Guide

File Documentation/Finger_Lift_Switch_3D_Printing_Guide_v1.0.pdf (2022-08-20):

V1.0 | July 2022

## Finger Lift Switch

## 3D PRINTING GUIDE

© 2022 by Neil Squire
This work is licensed under the CC BY SA 4.0 License: http://creativecommons.org/licenses/by-sa/4.0
Files available at https://makersmakingchange.com/project/finger-lift-switch/ | Page 1 of 3

### 3D Printing Summary

Metrics

Total Print Time (min) | 1:23
Total Number of Components | 6
Typical Total Mass (g) | 7
Typical Number of Print Setups | 1

### 3D Printing Settings

Print File Name | Qty | Total Print Time (hr:min ) | Mas s (g) | Infill (%) | Support(Y/ N) | Layer Height/ Nozzle Diameter(m m) | Notes (orientation, special settings, etc.)
Finger Lift Lever | 1 | 0:19 | 2 | 15 | N | 0.2/0.4 | -Print in orientation given in STL
Balance Screw Holder | 1 | 0:07 | 1 | 15 | N | 0.2/0.4 | -Print in orientation given in STL
Counterweigh t nut holder | 1 | 0:11 | 1 | 15 | N | 0.2/0.4 | -Print in orientation given in STL
Bearing Base & Bearing Base Cap | 1 | 0:29 | 2 | 15 | N | 0.2/0.4 | -Print in orientation given in STL
Reed Switch Plate | 1 | 0:10 | 1 | 15 | N | 0.2/0.4 | -Print in orientation given in STL

### Customization Options

Specific colours are not a requirement for this device, so device (or components) may be printed in whichever colours the user desires.

### Post-Processing

Remove any stranding or excess material in holes with a hobby knife. Any parts of the Finger Lift Pad that feel rough or scratchy should be lightly sanded with fine sandpaper until smooth to touch.

## 3D PRINTING GUIDE

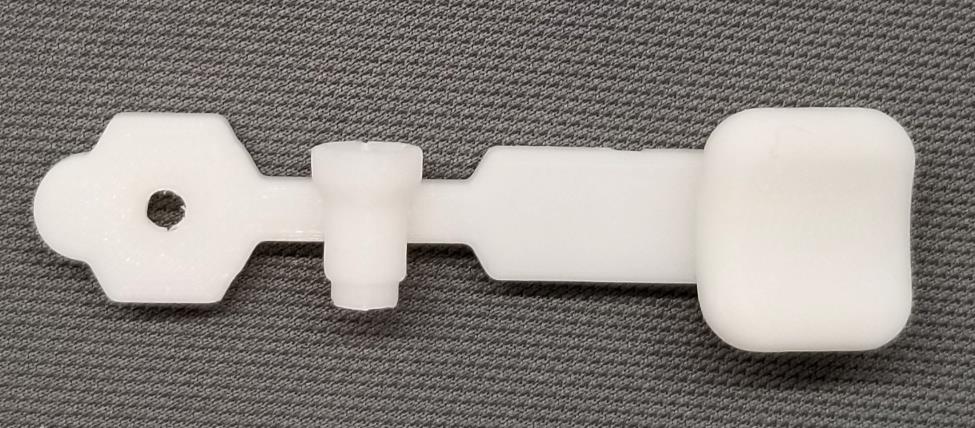
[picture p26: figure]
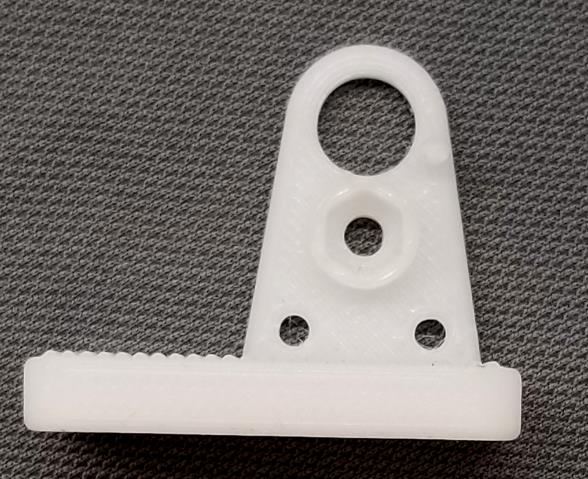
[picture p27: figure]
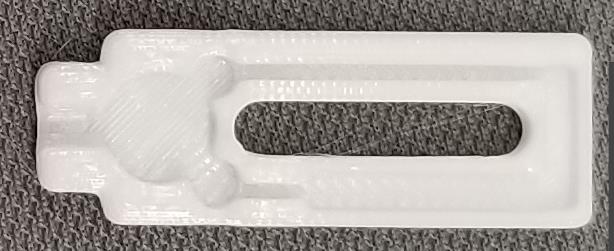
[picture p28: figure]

Files available at https://makersmakingchange.com/project/finger-lift-switch/ | Page 2 of 3

### Examples of Quality Prints

Finger Lift Lever

Bearing Base

Reed Switch Plate

Bearing Base Cap

## 3D PRINTING GUIDE

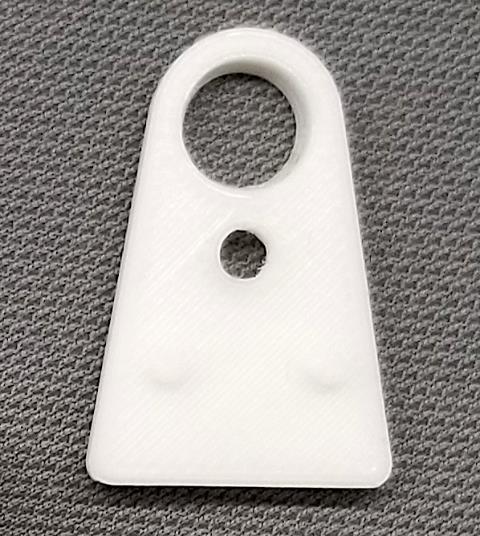
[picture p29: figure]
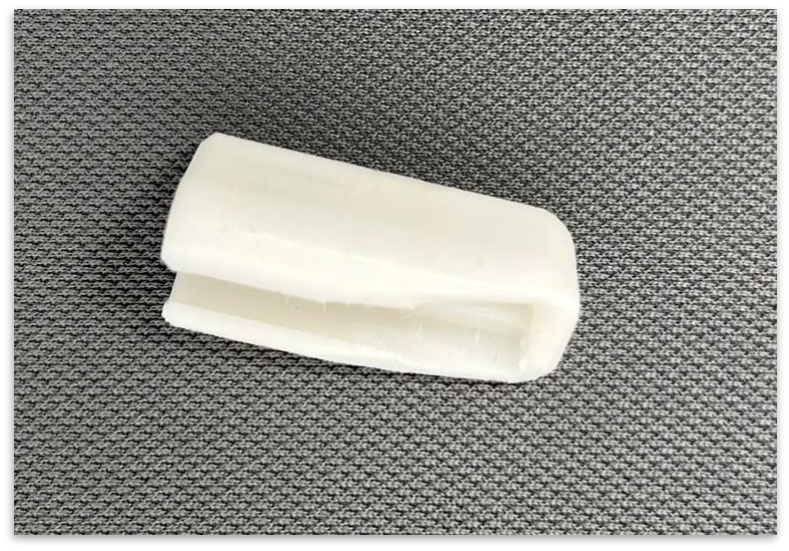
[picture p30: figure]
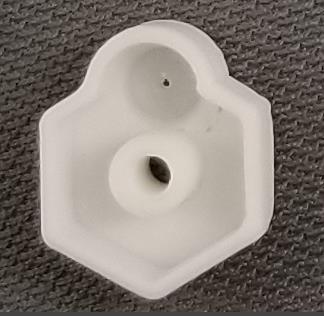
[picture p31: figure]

Files available at https://makersmakingchange.com/project/finger-lift-switch/ | Page 3 of 3

Balance Screw Holder

Counterweight nut holder

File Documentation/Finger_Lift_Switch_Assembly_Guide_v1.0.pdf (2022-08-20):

V1.0 | Aug 2022

## Finger Lift Switch

## ASSEMBLY GUIDE

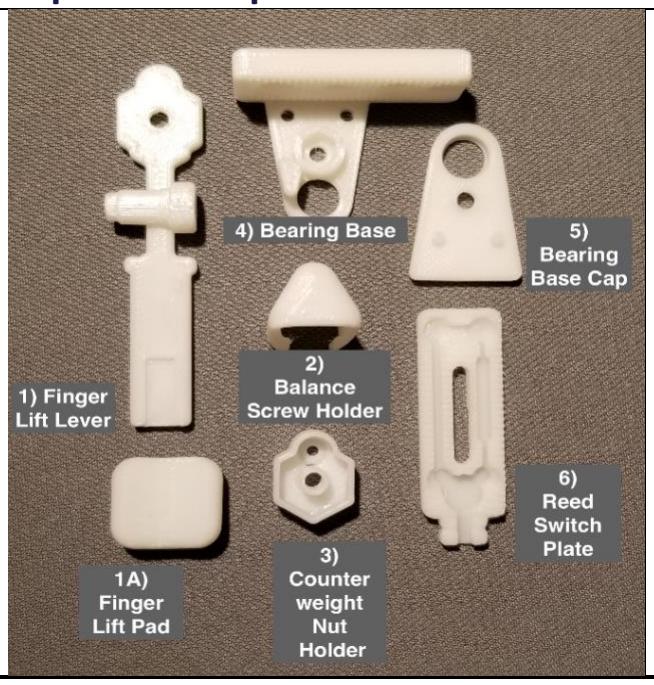
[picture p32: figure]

© 2022 by Neil Squire.

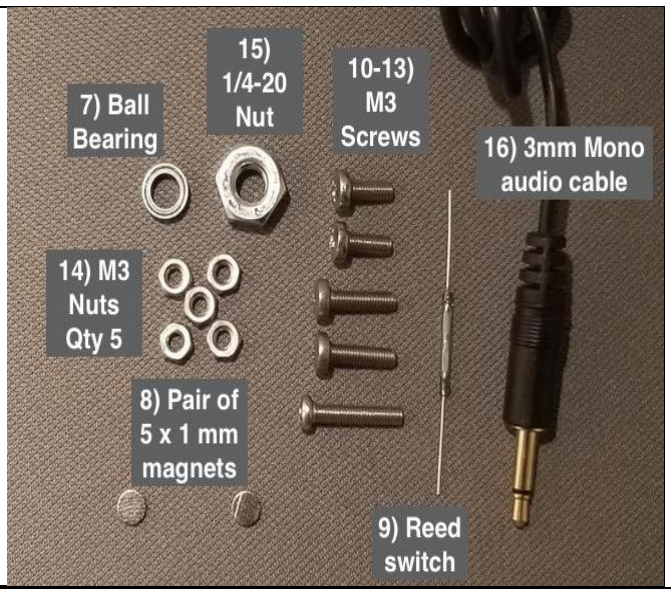
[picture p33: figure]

This work is licensed under the CC BY SA 4.0 License: http://creativecommons.org/licenses/by-sa/4.0
Files available at https://makersmakingchange.com/project/finger-lift-switch/ | Page 1 of 14

### Required Components

BOM
1. 1X Finger Lift Lever (3D) 1A. 1X Finger Lift Pad
2. 1X Balance Screw Holder (3D)
3. 1X Counterweight Nut Holder (3D)
4. 1X Bearing Base (3D)
5. 1X Bearing Base Cap (3D)
6. 1X Reed Switch Plate (3D)
7. 1X Ball Bearing: Type MR85ZZ (8 mm OD 5 mm ID)
8. 2X 5 mm x 1 mm Magnets (Neodymium)
9. 1X Reed Switch (Glass) Contact Normally Open (N/O) Magnetic Induction Switch (2 mm × 14 mm)
10. 2X M3 x 8 mm Stainless Steel screws (Base & Base Cap screws)
11. 1X M3 x 10 mm Stainless Steel screw (Counterweight screw)
12. 1X M3 x 12 mm Stainless Steel screw (Bearing Screw)
13. 1X M3 x 16 mm Stainless Steel screw (Balance screw)
14. 5X M3 Stainless Steel Nut
15. 1X 1/4-20 (Imperial size) Nut
16. 1X 5-foot mono audio cable with 3.5 mm male phono plug

## ASSEMBLY GUIDE

Files available at https://makersmakingchange.com/project/finger-lift-switch/ | Page 2 of 14

### Required Tools

- Soldering Iron (fine tip)
- 60/40 rosin core electrical solder
- Multimeter (with continuity reading capability)
- Medium size Phillips screwdriver (type #1)
- Side cutters
- Wire strippers
- Super glue (gel type is best)
- Hot melt glue gun (low temp type)
- Permanent felt marker (fine tip)
- Needle nose pliers
- Sturdy metal tweezers

### Required Personal Protective Equipment (PPE)

- Approved safety glasses

## ASSEMBLY GUIDE

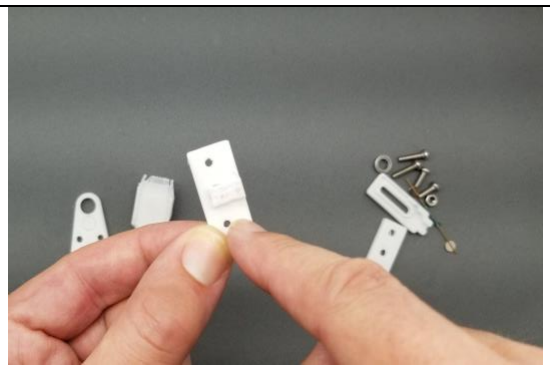
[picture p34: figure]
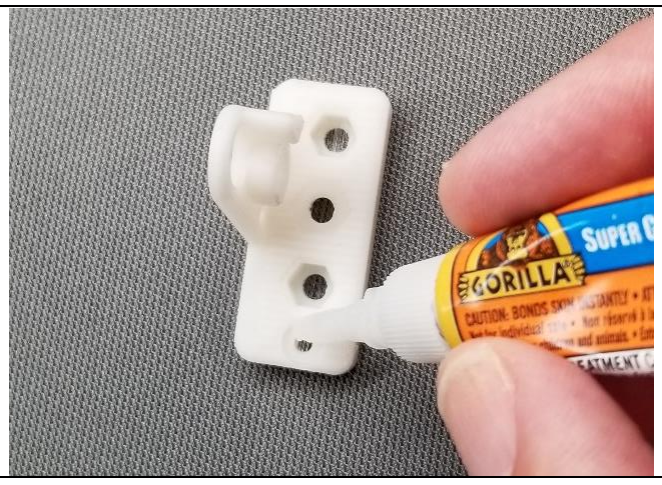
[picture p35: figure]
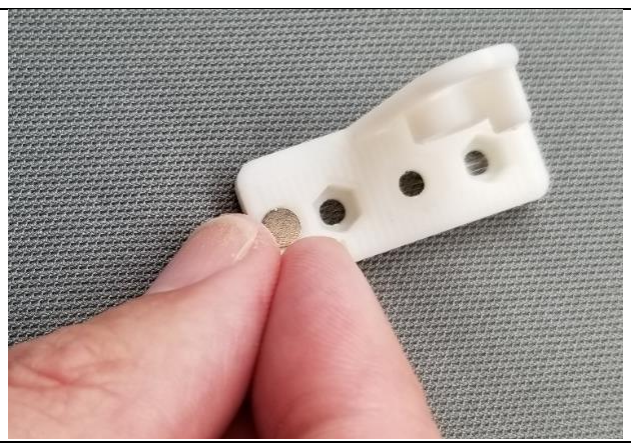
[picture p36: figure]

Files available at https://makersmakingchange.com/project/finger-lift-switch/ | Page 3 of 14

### Assembly Instructions

### Step 1

Remove any 3D support material using side cutters. Make sure the pad on the Finger Lift Lever is especially free of burrs that could irritate skin. If needed, use a bit of fine sandpaper (or emery cloth) to smooth the pad. Additionally, remove support material from any blocked holes or channels. Holes can also be cleared using a 2.5 mm drill bit (3/32 or #40 in Imperial units)

### Step 2

Apply a drop of superglue inside the corner magnet hole rim of the Bearing Base (Part #4 ).

### Step 3

Insert one of the 5 mm x 1 mm magnets (Part #8) into the corner magnet hole of the Bearing Base (Part #4). Wipe off any excess glue and allow glue a few minutes to set.

## ASSEMBLY GUIDE

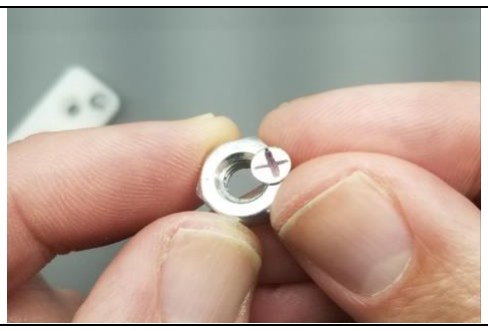
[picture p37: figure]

Files available at https://makersmakingchange.com/project/finger-lift-switch/ | Page 4 of 14

### Step 4

Place the second 5 mm x 1 mm magnet (Part #8) on top of the first glued magnet (don’t use glue for the second one!) and mark the top side with a fine felt tip permanent marker. This step is important, as it will mark the side of the second magnet that will repel the face of the glued magnet.

### Step 5

Take the top marked magnet from the marked side of the magnet and place it on the 1/4-20 nut. Make sure the marked side is on top.

### Step 6

Insert the nut (Part #8) and magnet (part #8) into the counterweight retainer (Part #3). Magnet side should go in first, with magnet in the rounded magnet slot, as shown in above photo.

Important: The marked side of the magnet must remain facing the plastic bottom well of the retainer.

### Step 7

Screw the counterweight retainer (Part #3) onto the Finger Lift Lever (Part #1) using an M3 x
10 mm screw (Part #11). Use one of the M3 nuts (Part #14) to capture the screw on the bottom side. Make sure the counterweight retainer goes on the same side of the lever arm as the bearing screw tube that straddles across it.

## ASSEMBLY GUIDE

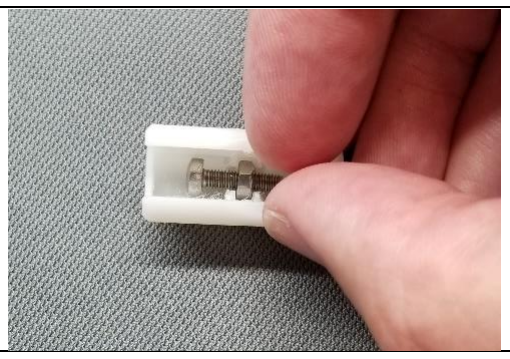
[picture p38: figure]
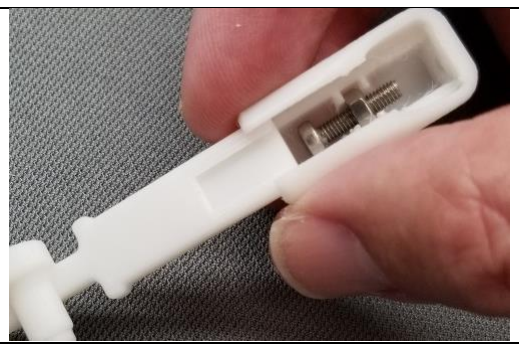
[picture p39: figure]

Files available at https://makersmakingchange.com/project/finger-lift-switch/ | Page 5 of 14

### Step 8

Insert one of the M3 nuts (Part #14) halfway onto an M3x12 screw and drop it into the slot of Balance Screw Holder (Part #2). Ensure that the screw head faces the small end hole, and that the top side of the nut is flat.

### Step 9

Slide Balance Screw Holder (Part #2) onto the Finger Lift Lever arm end (Part #1). Ensure the screw tip is facing towards the rounded end, as shown below on right.

### Step 10

Put a small drop of Superglue into each of the two ends of the Balance Screw Holder. This will bond the Balance Screw Holder onto Finger Lift Lever arm.

### Step 11

As a test, slide the Finger Lift Pad into the inner slider of the Finger Lift Lever, ensuring that the high side of the pad goes in first, as seen in the second image. Make sure the lift pad slides in all the way.

## ASSEMBLY GUIDE

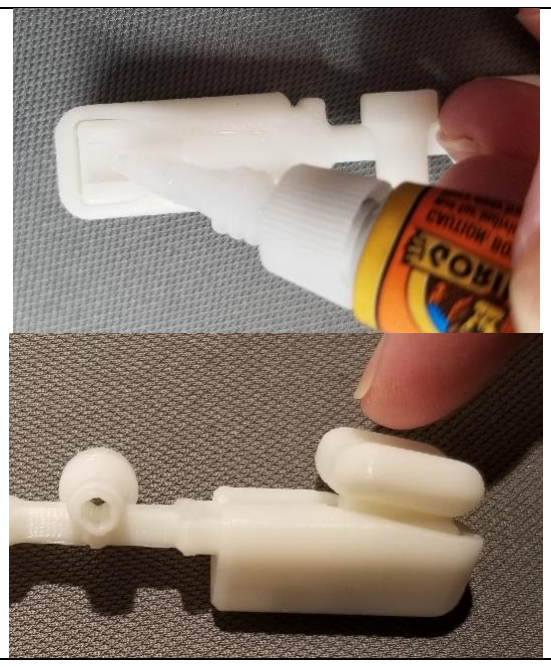
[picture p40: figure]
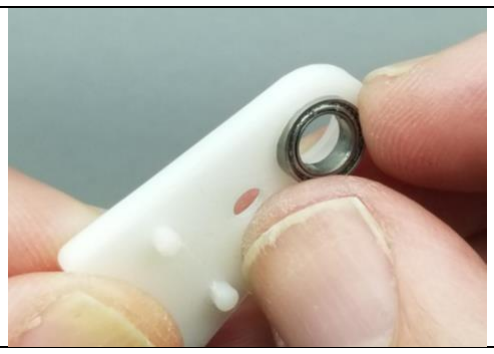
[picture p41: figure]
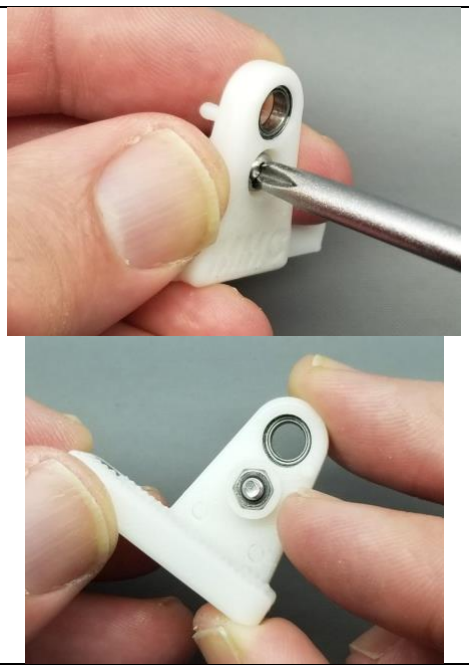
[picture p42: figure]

Files available at https://makersmakingchange.com/project/finger-lift-switch/ | Page 6 of 14

### Step 12

Slide out the finger lift pad and place a small drop of superglue at the end of the Finger Lift Lever where it was. Next, slide the finger lift pad back into place, in the same orientation as before. This completes the lever arm element.

### Step 13

Insert the MR85ZZ bearing (Part #7) into the large hole in the back of the Bearing Base Cap (Part #5, studded side). Make sure the bearing is properly aligned with the hole, or it may be difficult to insert.

### Step 14

Screw the bearing base cap (Part #5) onto the bearing base (Part #4) with an M3 X 8 mm screw (Part #12). Use one of the M3 nuts (Part #14) on the Bearing base side to hold the screw in place. This completes the Bearing Base element.

## ASSEMBLY GUIDE

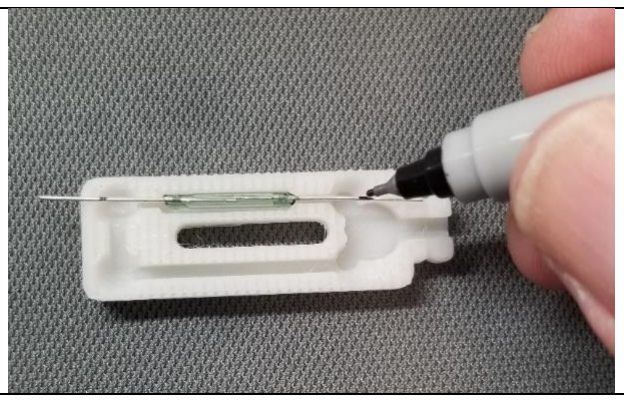
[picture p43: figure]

Files available at https://makersmakingchange.com/project/finger-lift-switch/ | Page 7 of 14

### Step 15

Lay the reed switch (Part #9) into the reed switch slot of the Reed Switch Plate (Part #6) as shown, and GENTLY mark the reed switch with a fine tip felt marker 1 mm shy of the solder cup edges.

### Step 16

Using needle nose pliers, firmly grip each end of the wire next to the cut marking on the reed switch side. Cut each wire end at the marked point, as shown in the image, with the needle nose pliers in the middle, to prevent wire strain from breaking the reed switch. IMPORTANT! Be extra careful not to place any pressure on the thin glass tube itself, as it is VERY easily broken.

### Step 17

Once the reed switch wires are trimmed, drop the reed switch (Part #9) into the Reed Switch Plate (Part #6). As one wire on the reed switch will be longer, flipping the reed switch will be needed if the reed switch got turned around. Ensure the reed switch drops in completely without pressure, and that the wire ends aren’t biting into the Reed Switch Plate.

### Step 18

Being careful not to nick the internal wires, use wire cutters to strip 42 mm of the outer insulation from the wire end of the 5-foot mono jack cable. Note that 42 mm is the same as the total length of the Reed Switch Plate, so you can use it as a ruler.

## ASSEMBLY GUIDE

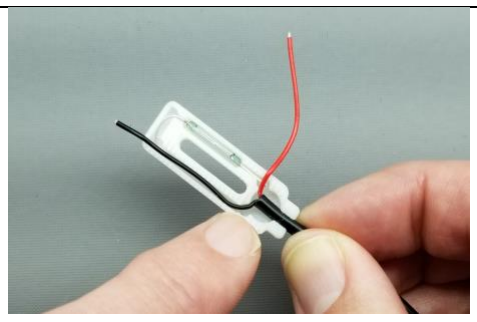
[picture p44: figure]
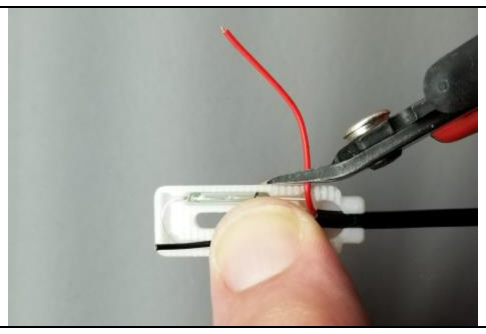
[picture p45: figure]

Files available at https://makersmakingchange.com/project/finger-lift-switch/ | Page 8 of 14

### Step 19

Insert the cable (Part #6) end into the Reed Switch Plate (Part #6) end hole until it hits the end of the screw slot. Hold it there. Tuck one wire into the long wire channel, and the other, over the side of the Reed switch plate where it crosses over the end of the reed switch (as in below photo). Note that wire color is not important for this application.

### Step 20

Using Side cutters, snip the wires where they cross over the edge of the Reed Switch Plate (Part #6).

### Step 21

Remove the 3.5 mm cable (Part #16) from the Reed Switch. Using wire strippers, strip 3 mm of insulation from each wire within the cable. Pinch the cable end as you strip to prevent pulling wire from the outer insulation.

### Step 22

Using a heated soldering iron, tin (pre-solder) the wire ends with 60/40 electrical solder. Use just enough solder to coat the wire ends while leaving a minimal solder blob on the end.

## ASSEMBLY GUIDE

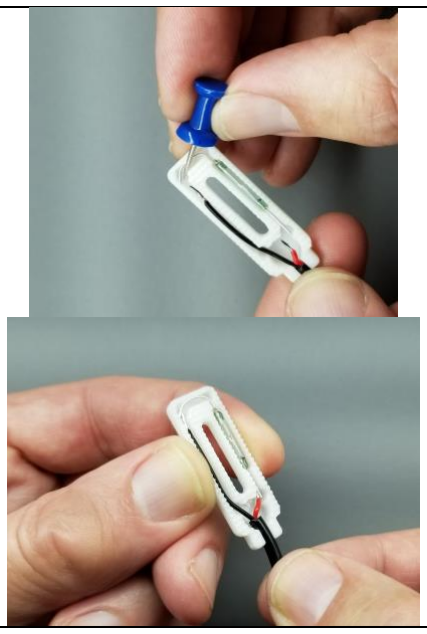
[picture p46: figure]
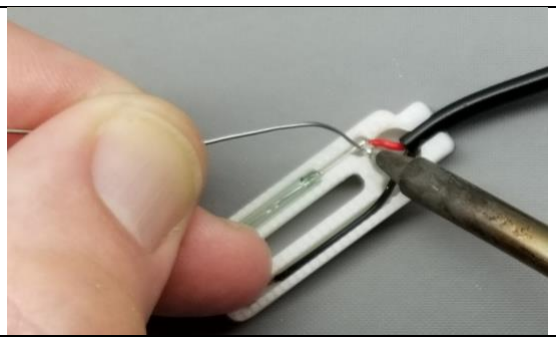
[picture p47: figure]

Files available at https://makersmakingchange.com/project/finger-lift-switch/ | Page 9 of 14

### Step 23

Return the prepared mono cable end into the Reed Switch Plate (Part #6), tucking the tinned wire ends under reed switch wire ends. Temporarily lift the reed switch wires with a push pin, or wire scrap, if necessary.

### Step 24

Solder the wire ends to the reed switch ends, on the Reed Switch Plate (Part #6), Solder as quickly as practical. Prolonged heat may weaken the magnetic properties of the reed switch or melt through the Reed Switch Plate plastic.

### Step 25

View the Reed Switch Plate (Part #6) from the side, to ensure no solder or wire protrudes above the grip edge. Use side cutters to cut off any excess solder blobs or protruding wires.

## ASSEMBLY GUIDE

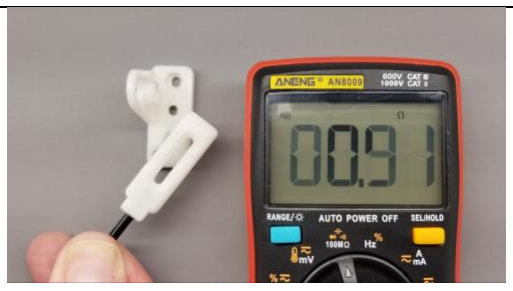
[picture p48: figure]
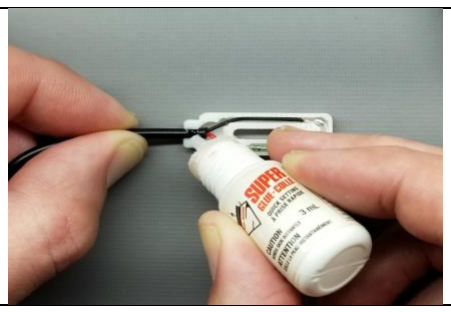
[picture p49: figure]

Files available at https://makersmakingchange.com/project/finger-lift-switch/ | Page 10 of 14

### Step 26

After soldering and trimming, it’s a good idea to test the reed switch using the magnet previously glued into the bearing base. Clip multimeter leads to the Mono plug contacts, set the multimeter to continuity, and enable the beeper (if possible). Bring the base magnet up against the cable end of the reed switch solder joint. Your multimeter should beep and/or show a low resistance reading. If all is well, it’s time to continue If not, it’s time to troubleshoot.

### Step 27

Add a drop of superglue to the cable end inside the Reed Switch Plate. Gently twist the cable back and forth 2-3 times, to work the glue around the full cable diameter.

### Step 28

Fill the reed carrier glue cavity (largest circle) with hot melt glue. Make sure the cable end is completely covered in glue, but don’t overfill, as the glue shouldn’t protrude above the plastic. If you get excess glue, use a side cutter to trim away excess glue once it has set.

## ASSEMBLY GUIDE

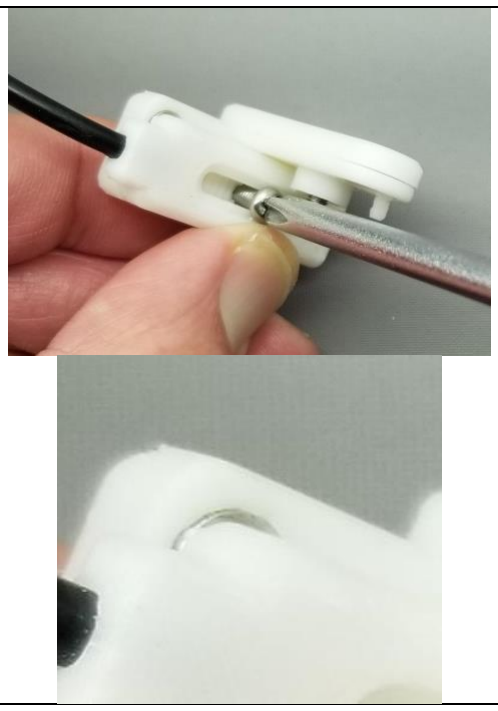
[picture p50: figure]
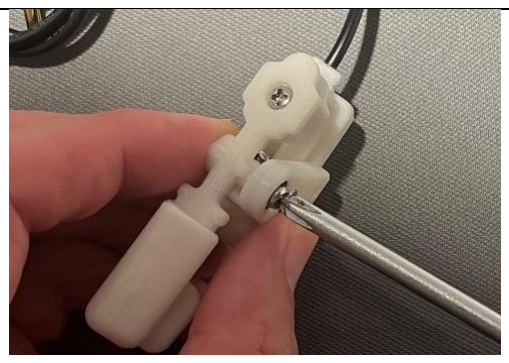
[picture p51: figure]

Files available at https://makersmakingchange.com/project/finger-lift-switch/ | Page 11 of 14

### Step 29

Add Preparation for mounting. Install the Reed Switch Plate onto the Bearing Base with an M3 x 8 mm screw, going through the M3 nut installed earlier. Position the Reed plate so that you see just a 1 mm crescent of the base magnet showing on back and side. Screw should only be kept finger tight.

### Step 30

Screw a M3 X 12 mm screw through the bearing, and through the shaft tube on the lever arm. Use one of the M3 nuts (Part 14) to capture the screw and secure the lever arm to the base. The screw should be finger tight, but still allow the lever arm to tilt without noticeable resistance. Make sure the screw head is centered within the outermost rim of the bearing. Note, the screw should be tightened just enough, to prevent side to motion of the lever arm.

## ASSEMBLY GUIDE

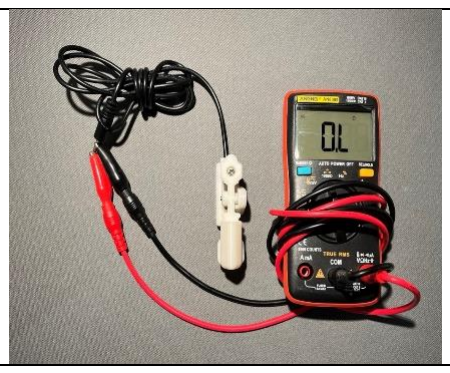
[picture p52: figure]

Files available at https://makersmakingchange.com/project/finger-lift-switch/ | Page 12 of 14

### Step 31

To complete the Finger Lift Switch, the reed switch plate needs to be adjusted for optimum performance. Using a narrow Phillips screwdriver, loosen the reed switch plate, just enough to allow it to slide forward (towards user) or back (towards cord end).

### Step 32

Setup your Finger Lift Switch for testing, by connecting a multimeter to the 3 mm plug end of the switch. Ensure the Multimeter is set to (lowest) ohms setting, and that the continuity feature is turned on (if your meter has this).

## ASSEMBLY GUIDE

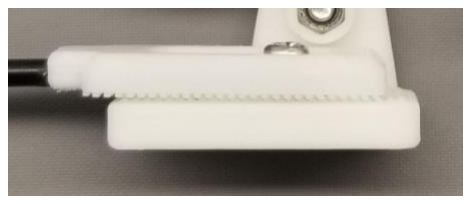
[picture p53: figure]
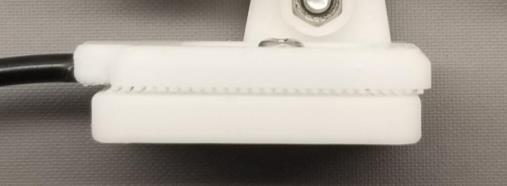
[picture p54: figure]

Files available at https://makersmakingchange.com/project/finger-lift-switch/ | Page 13 of 14

### Step 33

Using a multimeter set to continuity (or ohms), slide the reed switch plate to the position where it best triggers when the finger lift pad is lifted. At one extreme the switch will always be on, and at the other the switch will always be off. It may help to mark the extreme positions with a pencil, and then slide to the middle point between them. Note: you may need to ensure your screwdriver is removed during testing, as it may have magnetic properties that can interfere with calibration.

More sensitive

Typical

Less sensitive

### Step 34: Completion

Again, using the multimeter set to continuity, and leads connected to the plug, lift the finger pad to confirm proper operation of the switch. The switch is now complete. If you wish, you can test the on resistance of the switch by using the multimeter set to the ohms range. Ideally, the resistance of the switch should be below 1 ohm when on, but may be up to 12 ohms, depending on application.

## ASSEMBLY GUIDE

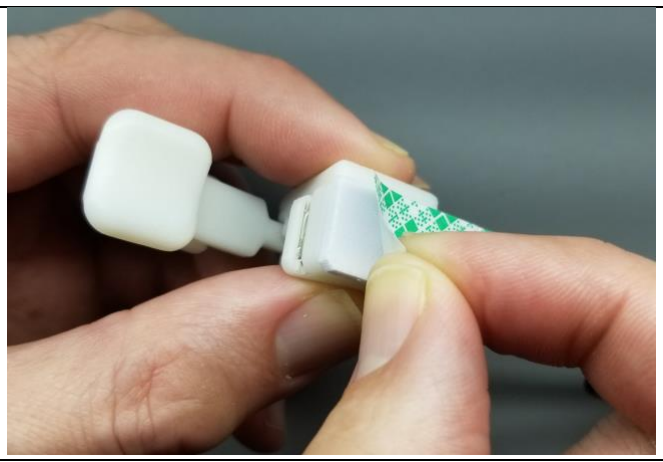
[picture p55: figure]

Files available at https://makersmakingchange.com/project/finger-lift-switch/ | Page 14 of 14

### Step 35: Optional Mounting Step

The finger lift switch can be mounted to a base plate (or splint) using double sided tape or hook and loop fastener (e.g., VELCRO). The use of hook and loop fasteners can allow for some minor repositioning of the switch if needed. Cut the tape to 34 x 14 mm.

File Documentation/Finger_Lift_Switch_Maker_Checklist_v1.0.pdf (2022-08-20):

V1.0 | July 2022

# Finger Lift Switch

## MAKER CHECKLIST

© 2022 by Neil Squire. (https://neilsquire.ca/) “Finger Lift Switch Maker Checklist” is licensed under the CC BY SA 4.0 License: http://creativecommons.org/licenses/bysa/4.0 (http://creativecommons.org/licenses/by-sa/4.0)
Design files available at https://www.makersmakingchange.com/project/finger-lift-switch/

## Maker To Do

☐ Order Hardware Components

☐ Ask User about color preferences

☐ Print 3D Printed Components

- 1 x Finger Lift Lever
- 1 x Finger Lift PAD
- 1 x Balance screw holder
- Counterweight nut holder
- Bearing Base & Bearing Base Cap
- Reed Switch Plate

☐ Assemble Switch

☐ Test Switch

☐ Clean and package Switch

☐ Print out Finger Lift Switch: Quick Guide

## Items for the User

☐ Tested, cleaned, and packaged Finger Lift

Switch

☐ Finger Lift Switch: Quick Guide
